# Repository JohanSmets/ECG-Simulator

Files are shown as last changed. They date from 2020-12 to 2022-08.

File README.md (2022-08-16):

# ECG-Simulator
 Electronics, Software and 3D Printable Enclosure of the ECG Patient Simulator based on an Atmega328.
 The simulator has 8 selectable heartrates going from 30 to 240 Bpm.  Works with a 9V battery and has an auto power off function.  This project consists of a Full KiCad project with schematic and PCB,  an Arduino sketch and all the 3D-printable files to make an enclosure.

 This project is licensed under Creative Commons Attribution Share-Alike International Licence 4.0

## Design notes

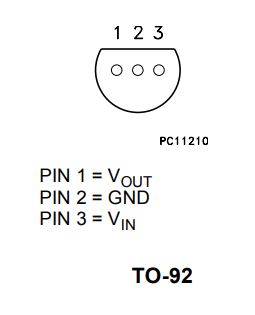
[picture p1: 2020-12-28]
Documentation/Data Sheets and Images/LE50ABZ 5V Regulator Bottom View.JPG

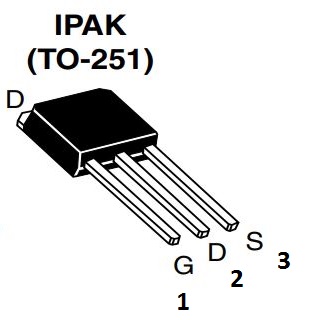
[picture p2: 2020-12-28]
Documentation/Data Sheets and Images/IRFU9024.JPG

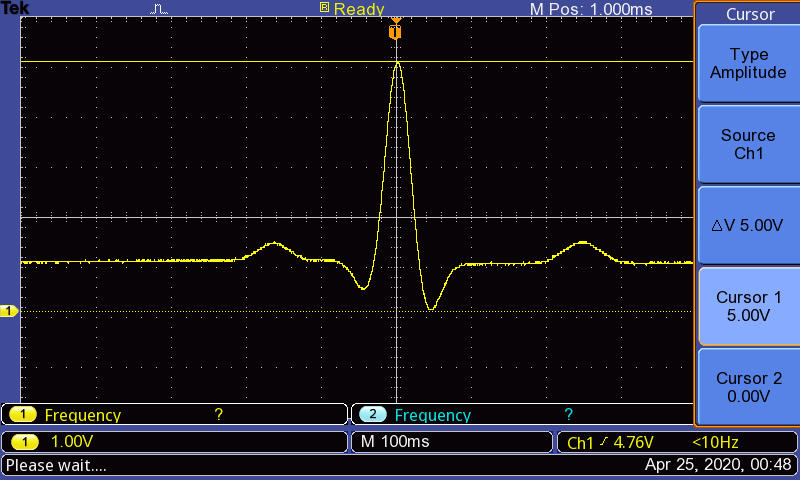
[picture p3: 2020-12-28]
SCOPE_WAVES/ECG Simulator/Signal out of function generator/F0003TEK.BMP

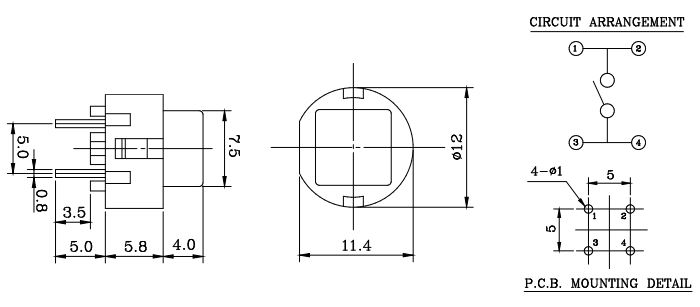
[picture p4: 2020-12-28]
Documentation/Data Sheets and Images/PushButton 532000007 Data.JPG

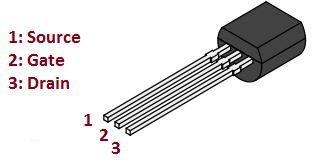
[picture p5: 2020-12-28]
Documentation/Data Sheets and Images/2N7000.JPG

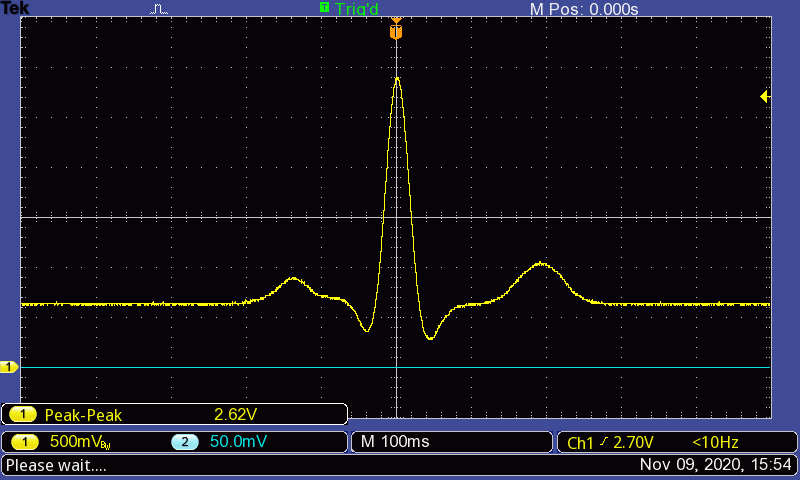
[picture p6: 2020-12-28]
SCOPE_WAVES/ECG Simulator/Signal behind Low Pass Filters with maximal gain selected/F0001TEK.BMP

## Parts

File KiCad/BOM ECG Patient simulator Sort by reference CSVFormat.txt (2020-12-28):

"Source:","C:\Users\Johan\Documents\Arduino\Projecten\ECG Simulator\KiCad ECG Patient simulator\ECG Patient simulator.sch"
"Date:","14/11/2020 13:45:55"
"Tool:","Eeschema (5.1.0)-1"
"Component Count:","41"
"Ref","Value","Footprint","Datasheet","Manufacturer","Vendor"
"C1","10uF","Capacitor_THT:CP_Radial_D6.3mm_P2.50mm","~","",""
"C2","2,2uF","Capacitor_THT:CP_Radial_D6.3mm_P2.50mm","~","",""
"C3","100nF","Capacitor_THT:C_Disc_D5.0mm_W2.5mm_P5.00mm","~","",""
"C4","100nF","Capacitor_THT:C_Disc_D5.0mm_W2.5mm_P5.00mm","~","",""
"C5","22pF","Capacitor_THT:C_Disc_D5.0mm_W2.5mm_P5.00mm","~","",""
"C6","22pF","Capacitor_THT:C_Disc_D5.0mm_W2.5mm_P5.00mm","~","",""
"C7","200nF","Capacitor_THT:C_Disc_D5.0mm_W2.5mm_P5.00mm","~","",""
"C8","47nF","Capacitor_THT:C_Disc_D5.0mm_W2.5mm_P5.00mm","~","",""
"C9","1uF","Capacitor_THT:CP_Radial_D6.3mm_P2.50mm","~","",""
"D1","1N4148","Diode_THT:D_DO-35_SOD27_P7.62mm_Horizontal","https://assets.nexperia.com/documents/data-sheet/1N4148_1N4448.pdf","",""
"D2","1N4148","Diode_THT:D_DO-35_SOD27_P7.62mm_Horizontal","https://assets.nexperia.com/documents/data-sheet/1N4148_1N4448.pdf","",""
"D3","1N4148","Diode_THT:D_DO-35_SOD27_P7.62mm_Horizontal","~","",""
"D4","1N4148","Diode_THT:D_DO-35_SOD27_P7.62mm_Horizontal","https://assets.nexperia.com/documents/data-sheet/1N4148_1N4448.pdf","",""
"D5","1N4001","Diode_THT:D_DO-41_SOD81_P10.16mm_Horizontal","http://www.vishay.com/docs/88503/1n4001.pdf","",""
"D6","LED","LED_THT:LED_D5.0mm","~","",""
"J1","Battery Connector","Connector_PinHeader_2.54mm:PinHeader_1x02_P2.54mm_Vertical","~","",""
"J2","LeadWire Connector","Connector_PinSocket_2.54mm:PinSocket_2x05_P2.54mm_Vertical","~","",""
"J3","Speaker Connector","Connector_PinHeader_2.54mm:PinHeader_1x02_P2.54mm_Vertical","~","",""
"J4","Att Resistor","Connector_PinHeader_2.54mm:PinHeader_1x05_P2.54mm_Vertical","~","",""
"Q1","IRFU9024","Package_TO_SOT_THT:TO-251-3_Vertical","","",""
"Q2","2N7000","Package_TO_SOT_THT:TO-92_Inline","https://www.fairchildsemi.com/datasheets/2N/2N7000.pdf","",""
"Q3","2N7000","Package_TO_SOT_THT:TO-92_Inline","https://www.fairchildsemi.com/datasheets/2N/2N7000.pdf","",""
"R1","56K","Resistor_THT:R_Axial_DIN0207_L6.3mm_D2.5mm_P10.16mm_Horizontal","~","",""
"R2","56K","Resistor_THT:R_Axial_DIN0207_L6.3mm_D2.5mm_P10.16mm_Horizontal","~","",""
"R3","220R","Resistor_THT:R_Axial_DIN0207_L6.3mm_D2.5mm_P10.16mm_Horizontal","~","",""
"R4","10K","Resistor_THT:R_Axial_DIN0207_L6.3mm_D2.5mm_P10.16mm_Horizontal","~","",""
"R5","5K6","Resistor_THT:R_Axial_DIN0207_L6.3mm_D2.5mm_P10.16mm_Horizontal","~","",""
"R6","2K7","Resistor_THT:R_Axial_DIN0207_L6.3mm_D2.5mm_P10.16mm_Horizontal","~","",""
"R7","10K","Resistor_THT:R_Axial_DIN0207_L6.3mm_D2.5mm_P10.16mm_Horizontal","~","",""
"R8","1K","Resistor_THT:R_Axial_DIN0207_L6.3mm_D2.5mm_P10.16mm_Horizontal","~","",""
"R9","330K","Resistor_THT:R_Axial_DIN0207_L6.3mm_D2.5mm_P10.16mm_Horizontal","~","",""
"R10","330R","Resistor_THT:R_Axial_DIN0207_L6.3mm_D2.5mm_P10.16mm_Horizontal","~","",""
"R11","27R","Resistor_THT:R_Axial_DIN0207_L6.3mm_D2.5mm_P10.16mm_Horizontal","~","",""
"R12","82R","Resistor_THT:R_Axial_DIN0207_L6.3mm_D2.5mm_P10.16mm_Horizontal","~","",""
"R13","390R","Resistor_THT:R_Axial_DIN0207_L6.3mm_D2.5mm_P10.16mm_Horizontal","~","",""
"SW1","UP","Button_Switch_THT:Push_E-Switch_KS01Q01","","",""
"SW2","DOWN","Button_Switch_THT:Push_E-Switch_KS01Q01","","",""
"SW4","DIP_x02","Package_DIP:DIP-4_W7.62mm","~","",""
"U1","ATmega328-PU","Package_DIP:DIP-28_W7.62mm","http://ww1.microchip.com/downloads/en/DeviceDoc/ATmega328_P%20AVR%20MCU%20with%20picoPower%20Technology%20Data%20Sheet%2040001984A.pdf","",""
"U2","LE50ABZ","Package_TO_SOT_THT:TO-92_Inline_Wide","","",""
"Y1","16Mhz","Crystal:Crystal_HC18-U_Vertical","~","",""

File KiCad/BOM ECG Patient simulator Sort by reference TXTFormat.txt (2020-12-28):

Source:	C:\Users\Johan\Documents\Arduino\Projecten\ECG Simulator\KiCad ECG Patient simulator\ECG Patient simulator.sch
Date:	14/11/2020 13:43:31
Tool:	Eeschema (5.1.0)-1
Component Count:	41
Ref	Value	Part	Footprint	Description	Vendor
C1	10uF	Device:CP	Capacitor_THT:CP_Radial_D6.3mm_P2.50mm	Polarized capacitor	
C2	2,2uF	Device:CP	Capacitor_THT:CP_Radial_D6.3mm_P2.50mm	Polarized capacitor	
C3	100nF	Device:C	Capacitor_THT:C_Disc_D5.0mm_W2.5mm_P5.00mm	Unpolarized capacitor	
C4	100nF	Device:C	Capacitor_THT:C_Disc_D5.0mm_W2.5mm_P5.00mm	Unpolarized capacitor	
C5	22pF	Device:C	Capacitor_THT:C_Disc_D5.0mm_W2.5mm_P5.00mm	Unpolarized capacitor	
C6	22pF	Device:C	Capacitor_THT:C_Disc_D5.0mm_W2.5mm_P5.00mm	Unpolarized capacitor	
C7	200nF	Device:C	Capacitor_THT:C_Disc_D5.0mm_W2.5mm_P5.00mm	Unpolarized capacitor	
C8	47nF	Device:C	Capacitor_THT:C_Disc_D5.0mm_W2.5mm_P5.00mm	Unpolarized capacitor	
C9	1uF	Device:CP_Small	Capacitor_THT:CP_Radial_D6.3mm_P2.50mm	Polarized capacitor, small symbol	
D1	1N4148	Diode:1N4148	Diode_THT:D_DO-35_SOD27_P7.62mm_Horizontal	100V 0.15A standard switching diode, DO-35	
D2	1N4148	Diode:1N4148	Diode_THT:D_DO-35_SOD27_P7.62mm_Horizontal	100V 0.15A standard switching diode, DO-35	
D3	1N4148	Device:D	Diode_THT:D_DO-35_SOD27_P7.62mm_Horizontal	Diode	
D4	1N4148	Diode:1N4148	Diode_THT:D_DO-35_SOD27_P7.62mm_Horizontal	100V 0.15A standard switching diode, DO-35	
D5	1N4001	Diode:1N4001	Diode_THT:D_DO-41_SOD81_P10.16mm_Horizontal	50V 1A General Purpose Rectifier Diode, DO-41	
D6	LED	Device:LED	LED_THT:LED_D5.0mm	Light emitting diode	
J1	Battery Connector	Connector_Generic:Conn_01x02	Connector_PinHeader_2.54mm:PinHeader_1x02_P2.54mm_Vertical	Generic connector, single row, 01x02, script generated (kicad-library-utils/schlib/autogen/connector/)	
J2	LeadWire Connector	Connector_Generic:Conn_02x05_Odd_Even	Connector_PinSocket_2.54mm:PinSocket_2x05_P2.54mm_Vertical	Generic connector, double row, 02x05, odd/even pin numbering scheme (row 1 odd numbers, row 2 even numbers), script generated (kicad-library-utils/schlib/autogen/connector/)	
J3	Speaker Connector	Connector_Generic:Conn_01x02	Connector_PinHeader_2.54mm:PinHeader_1x02_P2.54mm_Vertical	Generic connector, single row, 01x02, script generated (kicad-library-utils/schlib/autogen/connector/)	
J4	Att Resistor	Connector_Generic:Conn_01x05	Connector_PinHeader_2.54mm:PinHeader_1x05_P2.54mm_Vertical	Generic connector, single row, 01x05, script generated (kicad-library-utils/schlib/autogen/connector/)	
Q1	IRFU9024	Transistor_FET:IRFU9024	Package_TO_SOT_THT:TO-251-3_Vertical	-5A Id, -60V Vds, 0,28Ohm Rds, P-Channel MOSFET	
Q2	2N7000	Transistor_FET:2N7000	Package_TO_SOT_THT:TO-92_Inline	0.2A Id, 200V Vds, N-Channel MOSFET, 2.6V Logic Level, TO-92	
Q3	2N7000	Transistor_FET:2N7000	Package_TO_SOT_THT:TO-92_Inline	0.2A Id, 200V Vds, N-Channel MOSFET, 2.6V Logic Level, TO-92	
R1	56K	Device:R	Resistor_THT:R_Axial_DIN0207_L6.3mm_D2.5mm_P10.16mm_Horizontal	Resistor	
R2	56K	Device:R	Resistor_THT:R_Axial_DIN0207_L6.3mm_D2.5mm_P10.16mm_Horizontal	Resistor	
R3	220R	Device:R	Resistor_THT:R_Axial_DIN0207_L6.3mm_D2.5mm_P10.16mm_Horizontal	Resistor	
R4	10K	Device:R	Resistor_THT:R_Axial_DIN0207_L6.3mm_D2.5mm_P10.16mm_Horizontal	Resistor	
R5	5K6	Device:R	Resistor_THT:R_Axial_DIN0207_L6.3mm_D2.5mm_P10.16mm_Horizontal	Resistor	
R6	2K7	Device:R	Resistor_THT:R_Axial_DIN0207_L6.3mm_D2.5mm_P10.16mm_Horizontal	Resistor	
R7	10K	Device:R	Resistor_THT:R_Axial_DIN0207_L6.3mm_D2.5mm_P10.16mm_Horizontal	Resistor	
R8	1K	Device:R	Resistor_THT:R_Axial_DIN0207_L6.3mm_D2.5mm_P10.16mm_Horizontal	Resistor	
R9	330K	Device:R	Resistor_THT:R_Axial_DIN0207_L6.3mm_D2.5mm_P10.16mm_Horizontal	Resistor	
R10	330R	Device:R	Resistor_THT:R_Axial_DIN0207_L6.3mm_D2.5mm_P10.16mm_Horizontal	Resistor	
R11	27R	Device:R	Resistor_THT:R_Axial_DIN0207_L6.3mm_D2.5mm_P10.16mm_Horizontal	Resistor	
R12	82R	Device:R	Resistor_THT:R_Axial_DIN0207_L6.3mm_D2.5mm_P10.16mm_Horizontal	Resistor	
R13	390R	Device:R	Resistor_THT:R_Axial_DIN0207_L6.3mm_D2.5mm_P10.16mm_Horizontal	Resistor	
SW1	UP	Switch:SW_Push_Dual_x2	Button_Switch_THT:Push_E-Switch_KS01Q01	Push button switch, generic, separate symbols, four pins	
SW2	DOWN	Switch:SW_Push_Dual_x2	Button_Switch_THT:Push_E-Switch_KS01Q01	Push button switch, generic, separate symbols, four pins	
SW4	DIP_x02	Switch:SW_DIP_x02	Package_DIP:DIP-4_W7.62mm	2x DIP Switch, Single Pole Single Throw (SPST) switch, small symbol	
U1	ATmega328-PU	MCU_Microchip_ATmega:ATmega328-PU	Package_DIP:DIP-28_W7.62mm	20MHz, 32kB Flash, 2kB SRAM, 1kB EEPROM, DIP-28	
U2	LE50ABZ	Regulator_Linear:LE50ABZ	Package_TO_SOT_THT:TO-92_Inline_Wide	5V Voltage Regulator Low voltage Drop 100mA	
Y1	16Mhz	Device:Crystal	Crystal:Crystal_HC18-U_Vertical	Two pin crystal

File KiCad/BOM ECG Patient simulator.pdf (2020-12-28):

ECG Patient Simulator | BILL OF MATERIAL
Ref. | Quantity Type | Value | Footprint
C1 | 1 | Capacitor Electrolytic | 10uF | Capacitor_THT:CP_Radial_D6.3mm_P2.50mm
C2 | 1 | Capacitor Electrolytic | 2,2uF | Capacitor_THT:CP_Radial_D6.3mm_P2.50mm
C3, C4 | 2 | Capacitor Ceramic | 100nF | Capacitor_THT:C_Disc_D5.0mm_W2.5mm_P5.00mm
C5, C6 | 2 | Capacitor Ceramic | 22pF | Capacitor_THT:C_Disc_D5.0mm_W2.5mm_P5.00mm
C7 | 1 | Capacitor Ceramic | 200nF | Capacitor_THT:C_Disc_D5.0mm_W2.5mm_P5.00mm
C8 | 1 | Capacitor Electrolytic | 47nF | Capacitor_THT:C_Disc_D5.0mm_W2.5mm_P5.00mm
C9 | 1 | Capacitor Electrolytic | 1uF | Capacitor_THT:CP_Radial_D6.3mm_P2.50mm
D1, D2, D3, D4 | 4 | Diode DUS | 1N4148 | Diode_THT:D_DO-35_SOD27_P7.62mm_Horizontal
D5 | 1 | Diode Rectifier | 1N4001 or 1N4007 | Diode_THT:D_DO-41_SOD81_P10.16mm_Horizontal
D6 | 1 | LED White 5mm 3,2V 20mALED | LED_THT:LED_D5.0mm
J1 | 1 | PinConnector | Battery Connector | Connector_PinHeader_2.54mm:PinHeader_1x02_P2.54mm_Vertical
J2 | 1 | PinConnector | LeadWire Connector Connector_PinHeader_2.54mm:PinHeader_2x05_P2.54mm_Vertical
J3 | 1 | PinConnector | Speaker Connector | Connector_PinHeader_2.54mm:PinHeader_1x02_P2.54mm_Vertical
J4 | 1 | Att Resistor Socket | Att Resistor Socket | Connector_PinHeader_2.54mm:PinHeader_1x05_P2.54mm_Vertical
Q1 | 1 | MOSFET P-Channel | IRFU9024 | Package_TO_SOT_THT:TO-251-3_Vertical
Q2, Q3 | 2 | MOSFET N-Channel | 2N7000 | Package_TO_SOT_THT:TO-92_Inline
R1, R2 | 2 | Resistor 1/4W 5% | 56K | Resistor_THT:R_Axial_DIN0207_L6.3mm_D2.5mm_P10.16mm_Horizontal
R2 | 1 | Resistor 1/4W 5% | 56K | Resistor_THT:R_Axial_DIN0207_L6.3mm_D2.5mm_P10.16mm_Horizontal
R3 | 1 | Resistor 1/4W 5% | 220R | Resistor_THT:R_Axial_DIN0207_L6.3mm_D2.5mm_P10.16mm_Horizontal
R4, R7 | 2 | Resistor 1/4W 5% | 10K | Resistor_THT:R_Axial_DIN0207_L6.3mm_D2.5mm_P10.16mm_Horizontal
R5 | 1 | Resistor 1/4W 5% | 5K6 | Resistor_THT:R_Axial_DIN0207_L6.3mm_D2.5mm_P10.16mm_Horizontal
R6 | 1 | Resistor 1/4W 5% | 2K7 | Resistor_THT:R_Axial_DIN0207_L6.3mm_D2.5mm_P10.16mm_Horizontal
R8 | 1 | Resistor 1/4W 5% | 1K | Resistor_THT:R_Axial_DIN0207_L6.3mm_D2.5mm_P10.16mm_Horizontal
R9 | 1 | Resistor 1/4W 5% | 330K | Resistor_THT:R_Axial_DIN0207_L6.3mm_D2.5mm_P10.16mm_Horizontal
R10 | 1 | Resistor 1/4W 5% | 330R | Resistor_THT:R_Axial_DIN0207_L6.3mm_D2.5mm_P10.16mm_Horizontal

Date: 14/11/2020 13:43:31
Tool: Eeschema (5.1.0)-1
Component Count: 50

R11 | 1 | Resistor 1/4W 5% | 27R | Resistor_THT:R_Axial_DIN0207_L6.3mm_D2.5mm_P10.16mm_Horizontal
R12 | 1 | Resistor 1/4W 5% | 82R | Resistor_THT:R_Axial_DIN0207_L6.3mm_D2.5mm_P10.16mm_Horizontal
R13 | 1 | Resistor 1/4W 5% | 390R | Resistor_THT:R_Axial_DIN0207_L6.3mm_D2.5mm_P10.16mm_Horizontal
SW1, SW2 | 2 | PushButton BROSE 532.000.007 UP, DOWN Switch | Button_Switch_THT:Push_E-Switch_KS01Q01
SW4 | 1 | Dip Switch 2 position | DIP_x02 | Package_DIP:DIP-4_W7.62mm
U1 | 1 | Microcontroller Arduino Bootloaded ATmega328-PU | Package_DIP:DIP-28_W7.62mm
U2 | 1 | Linear Voltage regulator LE50ABZ | Package_TO_SOT_THT:TO-92_Inline_Wide
Y1 | 1 | Low Profile X-Tal | 16Mhz | Crystal:Crystal_HC18-U_Vertical

PCB and External Components
Speaker Att. Res | 1 | Resistor 1/4W 5% | Typically 100R | Resitor_THT:R_Axial_DIN0207_L6.3mm_D2.5mm_P10.16mm_Horizontal
9V Battery Clip | 1 | 9V Battery Clip
10-Pole IDC Connector1 | 10-Pole IDC Connector
20 mm Speaker | 1 | 20 mm Speaker | Piezo Speaker 20mm
28 Pin IC Socket | 1 | 28 Pin IC Socket | | Package_DIP:DIP-28_W7.62mm
Female Header | 2 | Female Header | | Female header for pushbutton extension
PCB Eurocircuits | 1 | PCB Eurocircuits

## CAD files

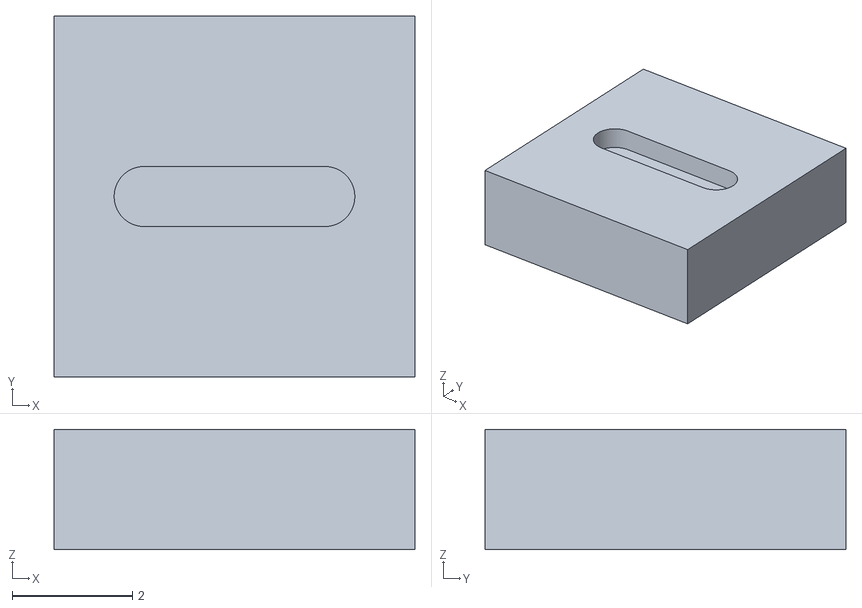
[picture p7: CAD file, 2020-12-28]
RS DesignSpark Mechanical/ECG Minus Inlay - Invallende Tekst.stl
6.00 x 6.00 x 2.00

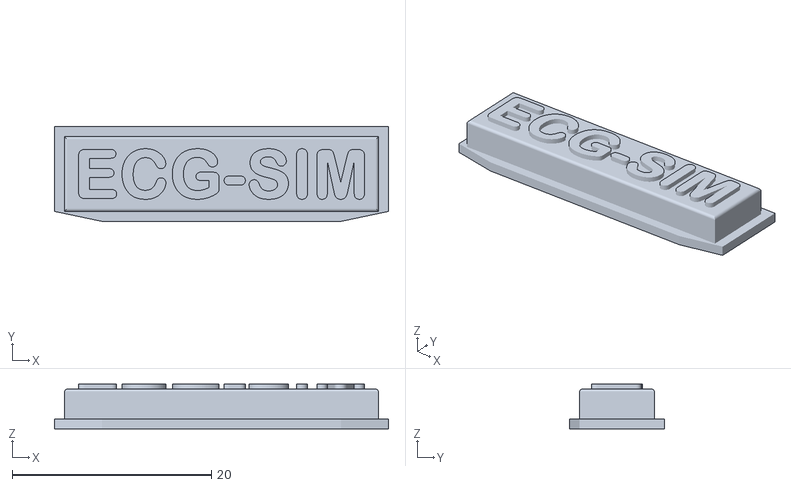
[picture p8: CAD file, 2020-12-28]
RS DesignSpark Mechanical/ECG ECG-SIM Inlay - Opliggende Tekst.stl
33.5 x 9.50 x 4.50

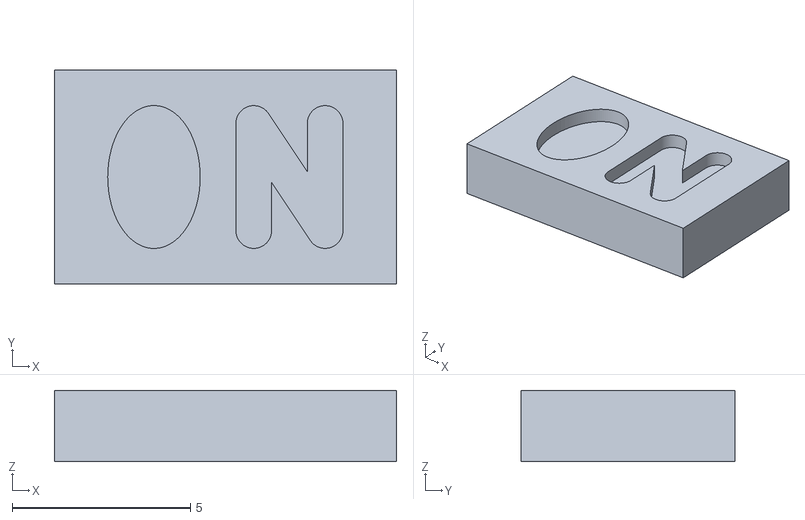
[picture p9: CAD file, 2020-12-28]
RS DesignSpark Mechanical/ECG ON inlay - Invallende Tekst.stl
9.58 x 6.00 x 2.00

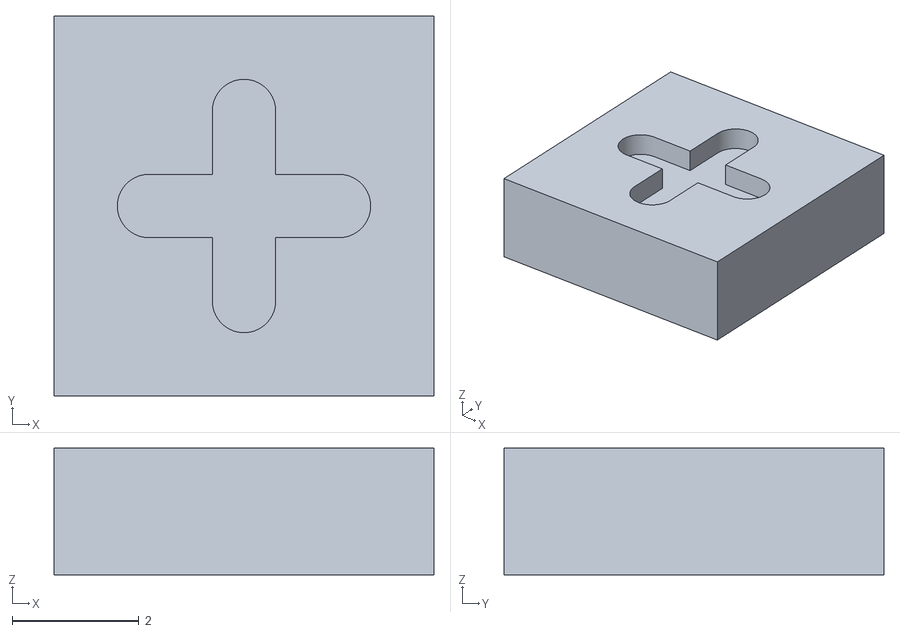
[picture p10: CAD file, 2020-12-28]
RS DesignSpark Mechanical/ECG Plus Inlay - Invallende Tekst.stl
6.00 x 6.00 x 2.00

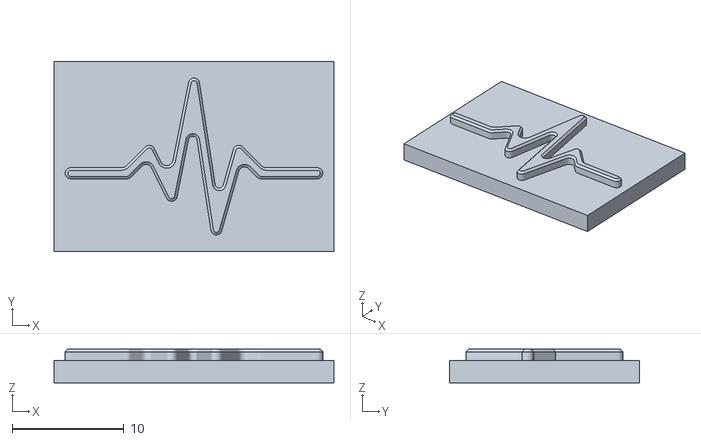
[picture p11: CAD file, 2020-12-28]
RS DesignSpark Mechanical/ECG WaveForm Inlay.stl
25.0 x 17.0 x 3.00

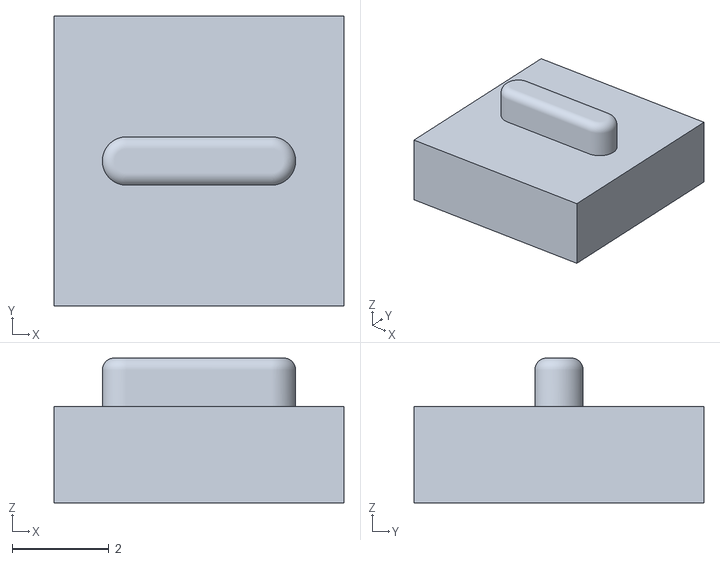
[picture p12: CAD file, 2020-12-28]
RS DesignSpark Mechanical/ECG Minus Inlay - Opliggende Tekst.stl
6.00 x 6.00 x 3.00

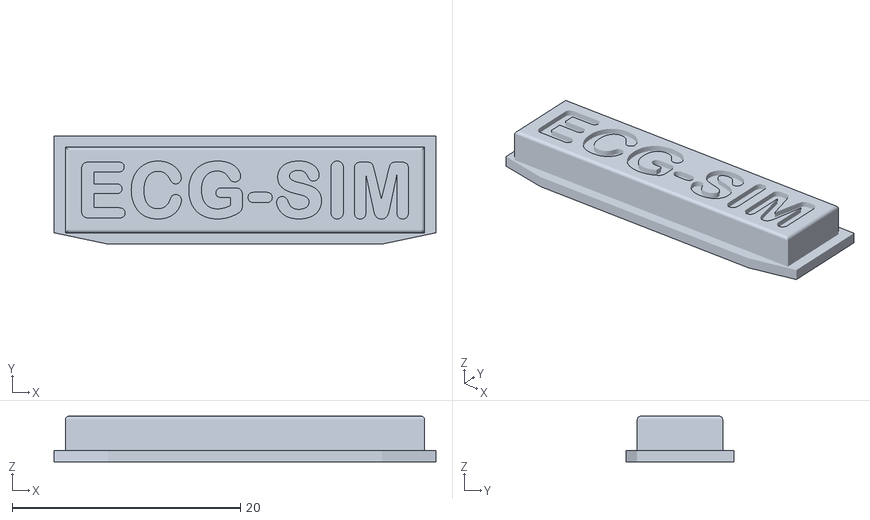
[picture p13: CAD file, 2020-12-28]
RS DesignSpark Mechanical/ECG ECG-SIM Inlay - Invallende Tekst.stl
33.5 x 9.50 x 4.00

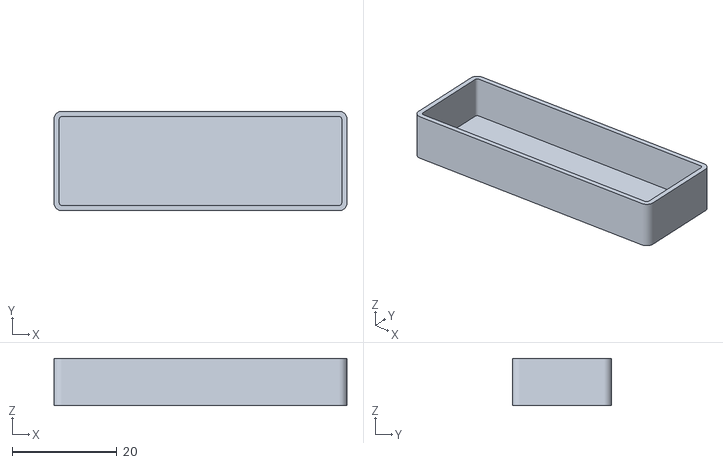
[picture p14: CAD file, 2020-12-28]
RS DesignSpark Mechanical/ECG Battery Cover.stl
56.0 x 19.0 x 9.00

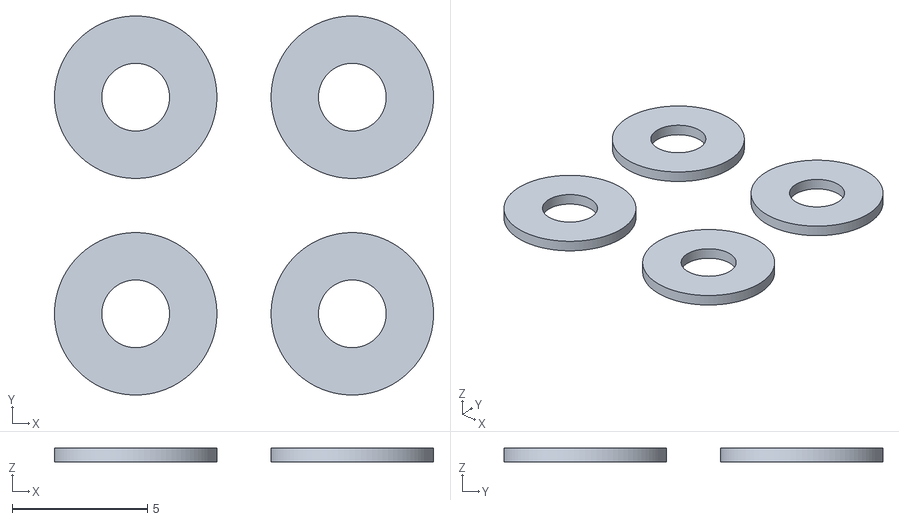
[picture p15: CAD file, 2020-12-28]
RS DesignSpark Mechanical/Afstandsbusjes 2_5 mm - 6_0 mm - H 0_5 mm (4 Stuks).stl
14.0 x 14.0 x 0.5

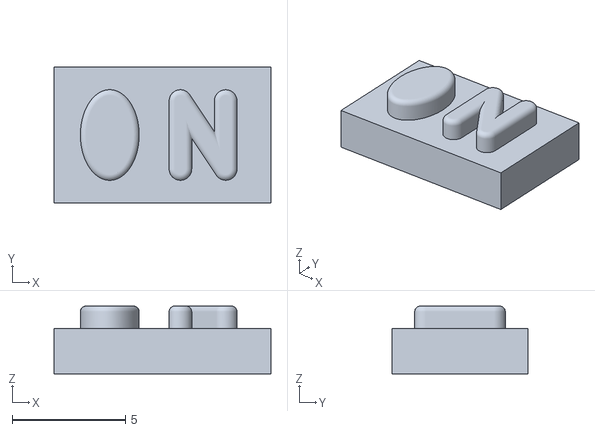
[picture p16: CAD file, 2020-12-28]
RS DesignSpark Mechanical/ECG ON inlay - Opliggende Tekst.stl
9.58 x 6.00 x 3.00

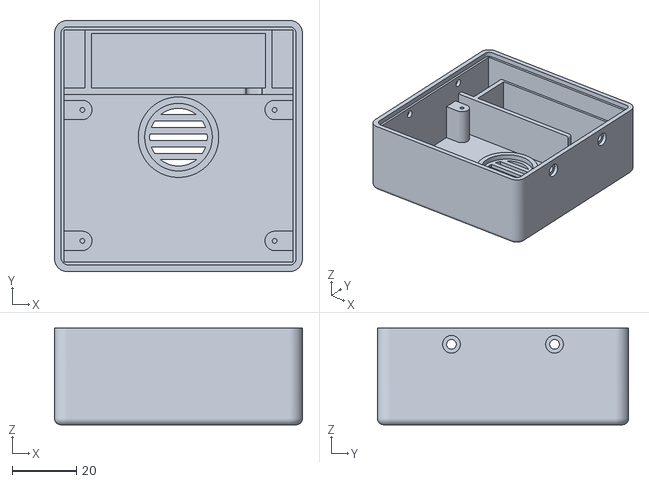
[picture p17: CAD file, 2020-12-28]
RS DesignSpark Mechanical/ECG Bottom Case.stl
77.0 x 78.0 x 30.0

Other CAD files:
RS DesignSpark Mechanical/ECG Plus Inlay - Opliggende Tekst.stl

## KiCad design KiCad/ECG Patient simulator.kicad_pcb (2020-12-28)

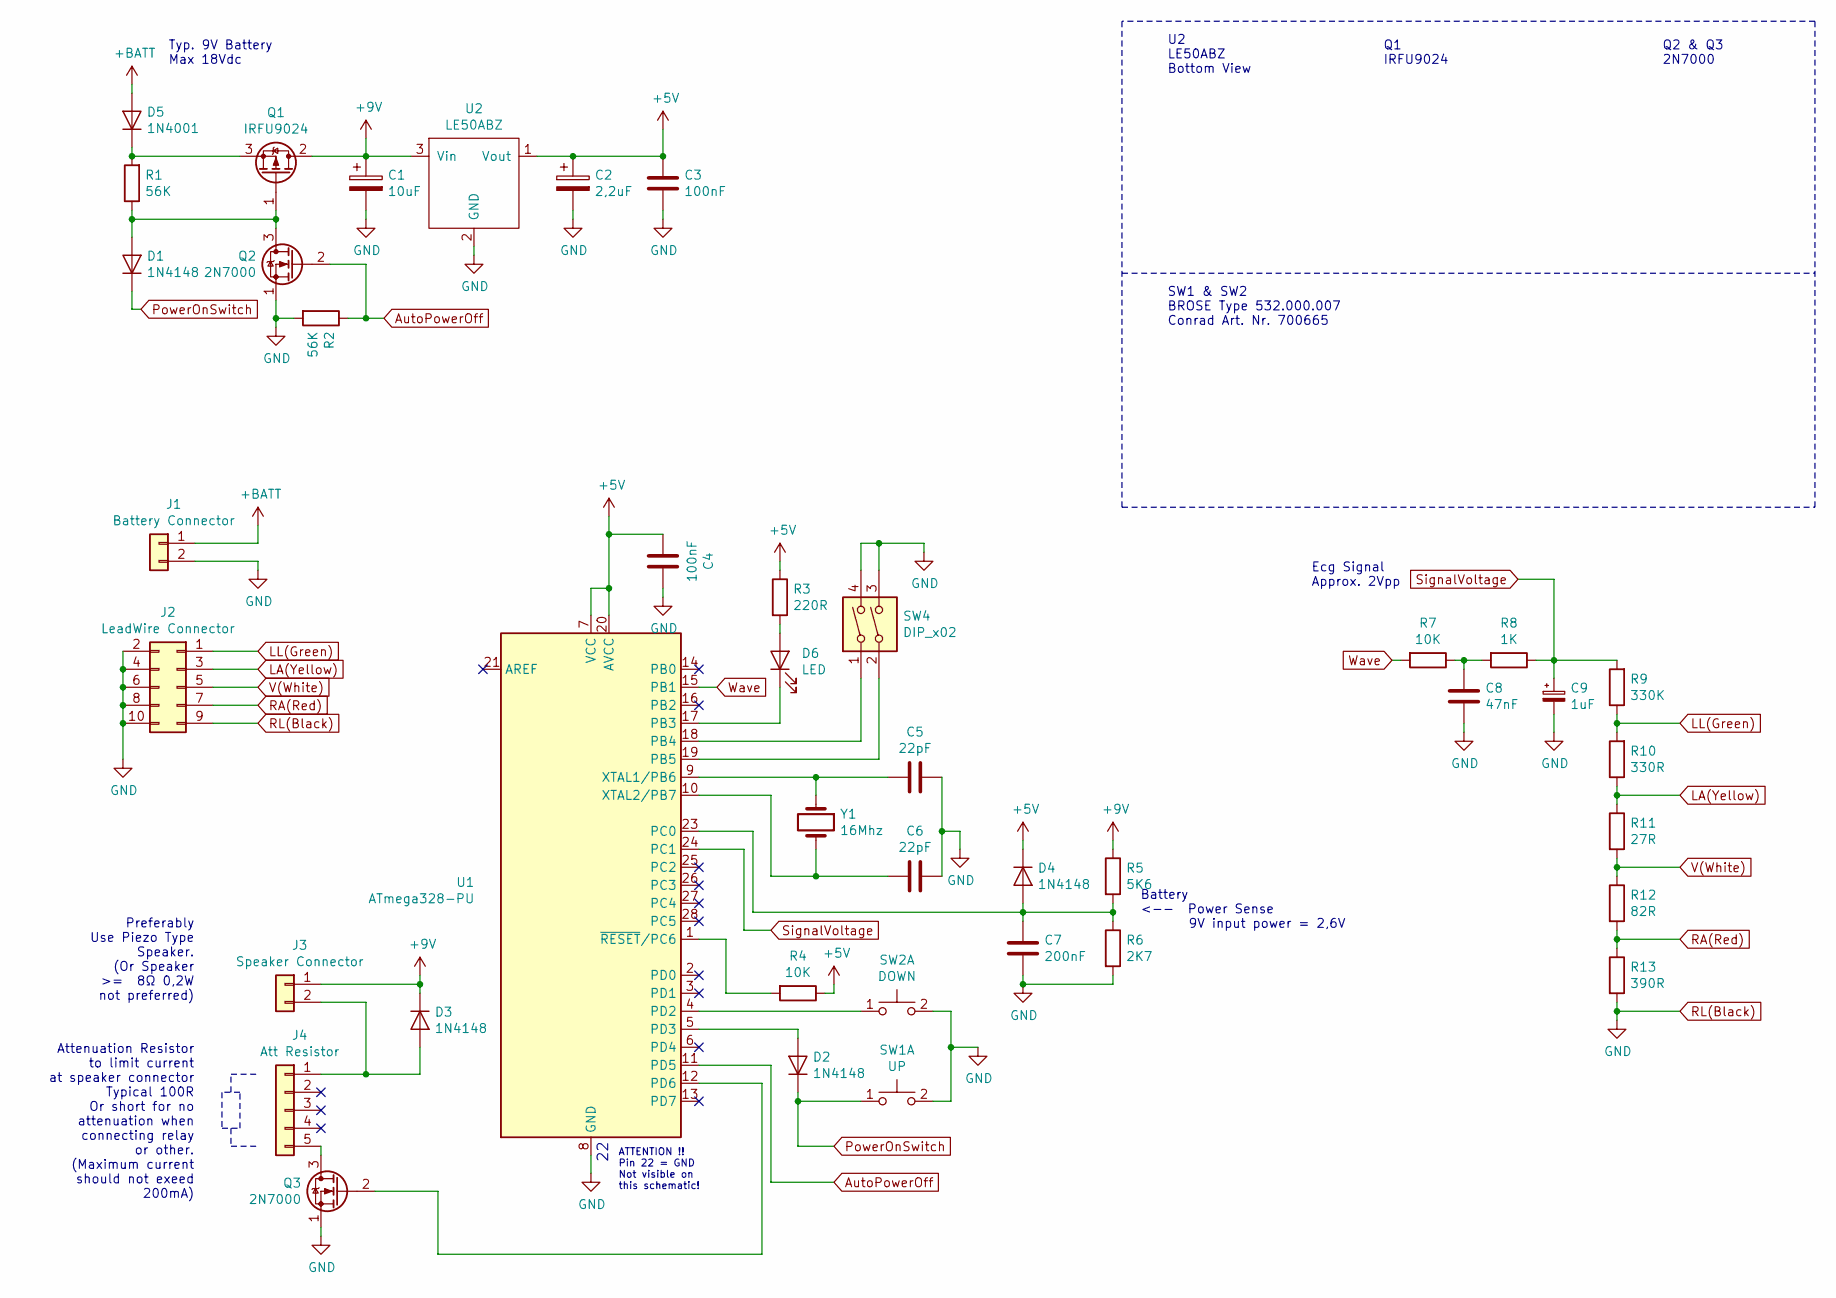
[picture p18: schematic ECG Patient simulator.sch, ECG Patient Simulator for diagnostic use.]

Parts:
C1: 10uF; CP_Radial_D6.3mm_P2.50mm
C2: 2,2uF; CP_Radial_D6.3mm_P2.50mm
C3, C4: 100nF; C_Disc_D5.0mm_W2.5mm_P5.00mm
C5, C6: 22pF; C_Disc_D5.0mm_W2.5mm_P5.00mm
C7: 200nF; C_Disc_D5.0mm_W2.5mm_P5.00mm
C8: 47nF; C_Disc_D5.0mm_W2.5mm_P5.00mm
C9: 1uF; CP_Radial_D6.3mm_P2.50mm
D1, D2, D3, D4: 1N4148; D_DO-35_SOD27_P7.62mm_Horizontal
D5: 1N4001; D_DO-41_SOD81_P10.16mm_Horizontal
D6: LED; LED_D5.0mm
J1: Battery Connector; PinHeader_1x02_P2.54mm_Vertical
J2: LeadWire Connector; PinSocket_2x05_P2.54mm_Vertical
J3: Speaker Connector; PinHeader_1x02_P2.54mm_Vertical
J4: Att Resistor; PinHeader_1x05_P2.54mm_Vertical
Q1: IRFU9024; TO-251-3_Vertical
Q2, Q3: 2N7000; TO-92_Inline
R1, R2: 56K; R_Axial_DIN0207_L6.3mm_D2.5mm_P10.16mm_Horizontal
R3: 220R; R_Axial_DIN0207_L6.3mm_D2.5mm_P10.16mm_Horizontal
R4, R7: 10K; R_Axial_DIN0207_L6.3mm_D2.5mm_P10.16mm_Horizontal
R5: 5K6; R_Axial_DIN0207_L6.3mm_D2.5mm_P10.16mm_Horizontal
R6: 2K7; R_Axial_DIN0207_L6.3mm_D2.5mm_P10.16mm_Horizontal
R8: 1K; R_Axial_DIN0207_L6.3mm_D2.5mm_P10.16mm_Horizontal
R9: 330K; R_Axial_DIN0207_L6.3mm_D2.5mm_P10.16mm_Horizontal
R10: 330R; R_Axial_DIN0207_L6.3mm_D2.5mm_P10.16mm_Horizontal
R11: 27R; R_Axial_DIN0207_L6.3mm_D2.5mm_P10.16mm_Horizontal
R12: 82R; R_Axial_DIN0207_L6.3mm_D2.5mm_P10.16mm_Horizontal
R13: 390R; R_Axial_DIN0207_L6.3mm_D2.5mm_P10.16mm_Horizontal
SW1: UP; Push_E-Switch_KS01Q01
SW2: DOWN; Push_E-Switch_KS01Q01
SW4: DIP_x02; DIP-4_W7.62mm
U1: ATmega328-PU; DIP-28_W7.62mm
U2: LE50ABZ; TO-92_Inline_Wide
Y1: 16Mhz; Crystal_HC18-U_Vertical

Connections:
+5V: C2.1, C3.1, C4.2, D4.1 (K), R3.1, R4.1, U1.7 (VCC), U1.20 (AVCC), U2.1 (Vout)
+9V: C1.1, D3.1 (K), J3.1, Q1.2 (D), R5.1, U2.3 (Vin); also elsewhere on the board
+BATT: D5.2 (A), J1.1; also elsewhere on the board
AutoPowerOff: Q2.2 (G), R2.1, U1.11 (PD5)
LA(Yellow): J2.3, R10.1, R11.1
LL(Green): J2.1, R9.1, R10.2
unnamed: C5.2, U1.9 (XTAL1/PB6), Y1.1
unnamed: C6.2, U1.10 (XTAL2/PB7), Y1.2
unnamed: C7.1, D4.2 (A), R5.2, R6.1, U1.23 (PC0)
unnamed: C8.1, R7.1, R8.2
unnamed: D1.2 (A), Q1.1 (G), Q2.3 (D), R1.1
unnamed: D2.2 (A), U1.5 (PD3)
unnamed 12: D3.2 (A), J3.2, J4.1; also elsewhere on the board
unnamed: D5.1 (K), Q1.3 (S), R1.2
unnamed: D6.1 (K), U1.17 (PB3)
unnamed: D6.2 (A), R3.2
unnamed: J4.5, Q3.3 (D)
unnamed: Q3.2 (G), U1.12 (PD6)
unnamed: R4.2, U1.1 (~RESET~/PC6)
unnamed: SW2.1 (C), U1.4 (PD2)
unnamed: SW4.1, U1.18 (PB4)
unnamed: SW4.2, U1.19 (PB5)
PowerOnSwitch: D1.1 (K), D2.1 (K), SW1.1 (C)
RA(Red): J2.7, R12.2, R13.1
RL(Black): C1.2, C2.2, C3.2, C4.1, C5.1, C6.1, C7.2, C8.2, C9.2, J1.2, J2.2, J2.4, J2.6, J2.8, J2.9, J2.10, Q2.1 (S), Q3.1 (S), R2.2, R6.2, R13.2, SW1.2 (D), SW2.2 (D), SW4.3, SW4.4, U1.8 (GND), U1.22 (GND), U2.2 (GND); also elsewhere on the board
SignalVoltage: C9.1, R8.1, R9.2, U1.24 (PC1)
V(White): J2.5, R11.2, R12.1
Wave: R7.2, U1.15 (PB1)

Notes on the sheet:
Battery <-- Power Sense 9V input power = 2,6V
Typ. 9V Battery Max 18Vdc
U2 LE50ABZ Bottom View
Q1 IRFU9024
Q2 & Q3 2N7000
SW1 & SW2 BROSE Type 532.000.007 Conrad Art. Nr. 700665
ATTENTION !! Pin 22 = GND Not visible on this schematic!
Ecg Signal Approx. 2Vpp
Preferably Use Piezo Type Speaker. (Or Speaker >= 8Ω 0,2W not preferred)
Attenuation Resistor to limit current at speaker connector Typical 100R Or short for no attenuation when connecting relay or other. (Maximum current should not exeed 200mA)

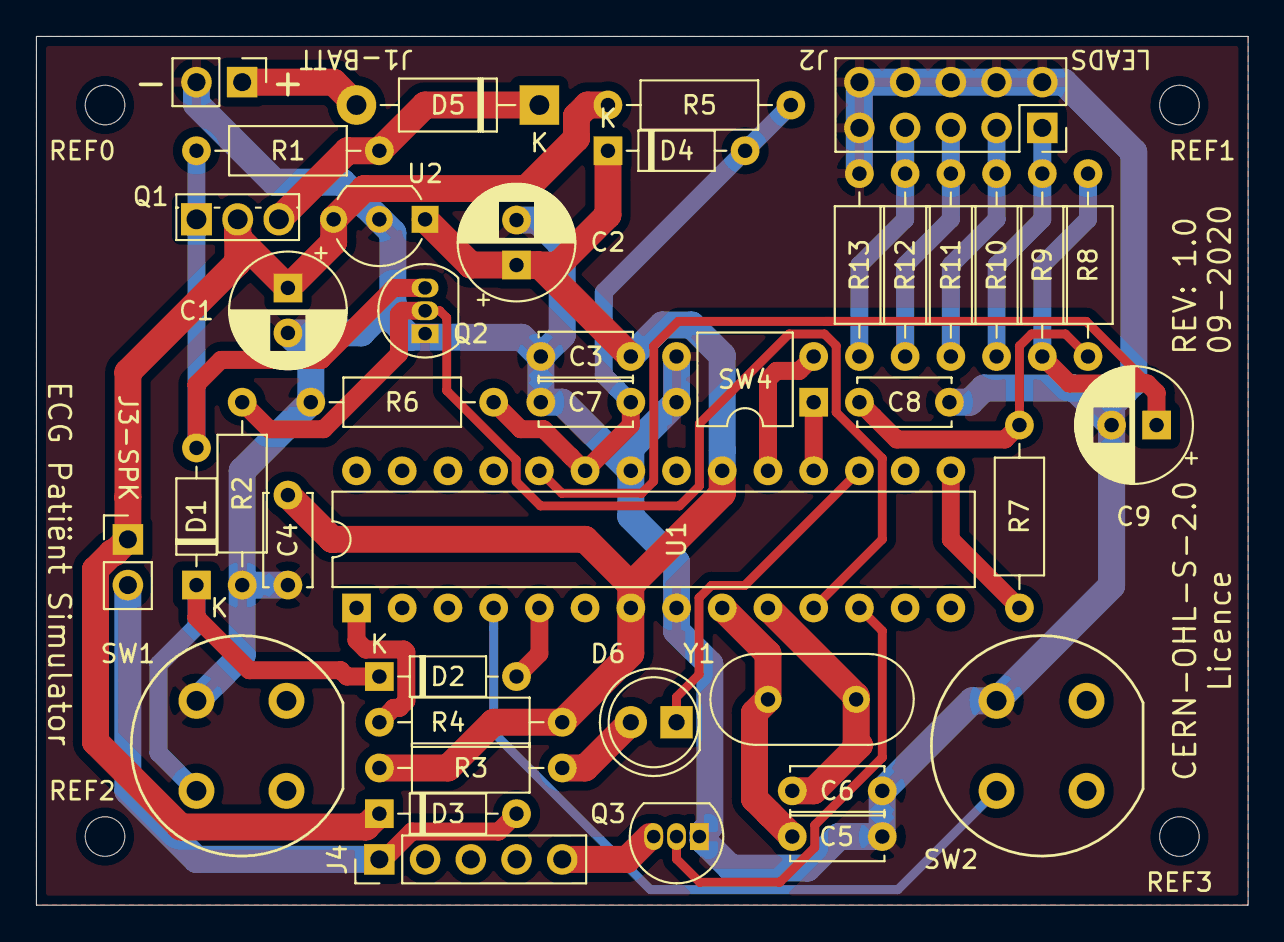
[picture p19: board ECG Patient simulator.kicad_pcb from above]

Board: 2 copper layers, 67.3 x 48.3 mm, 45 parts (0 on the bottom side), 28 nets.

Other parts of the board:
J1-BATT: Battery Connector; PinHeader_1x02_P2.54mm_Vertical
J3-SPK: Speaker Connector; PinHeader_1x02_P2.54mm_Vertical
REF0, REF1, REF2, REF3: MountingHole_2.2mm_M2_ISO7380

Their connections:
+9V: J3-SPK.1; also elsewhere on the board
+BATT: J1-BATT.1; also elsewhere on the board
unnamed 12: J3-SPK.2; also elsewhere on the board
RL(Black): J1-BATT.2; also elsewhere on the board

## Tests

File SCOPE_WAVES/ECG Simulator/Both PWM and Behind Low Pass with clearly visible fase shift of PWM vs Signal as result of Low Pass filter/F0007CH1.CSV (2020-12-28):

Record Length | 2.500000e+03 | -0.122000000000 | 0.00000
Sample Interval | 1.000000e-04 | -0.121900000000 | 0.00000
Trigger Point | 1.220000000000e+03 | -0.121800000000 | 0.00000
 |  | -0.121700000000 | 0.00000
 |  | -0.121600000000 | 50.00000
 |  | -0.121500000000 | 50.00000
Source | CH1 | -0.121400000000 | 0.00000
Vertical Units | V | -0.121300000000 | 0.00000
Vertical Scale | 5.000000e+01 | -0.121200000000 | 0.00000
Vertical Offset | 8.800000e+01 | -0.121100000000 | 0.00000
Horizontal Units | s | -0.121000000000 | 0.00000
Horizontal Scale | 2.500000e-02 | -0.120900000000 | 0.00000
Pt Fmt | Y | -0.120800000000 | 50.00000
Yzero | 0.000000e+00 | -0.120700000000 | 0.00000
Probe Atten | 1.000000e+01 | -0.120600000000 | 2.00000
Model Number | TBS1102B | -0.120500000000 | 2.00000
Serial Number | C021706 | -0.120400000000 | 0.00000
Firmware Version | FV:v4.06 | -0.120300000000 | 0.00000
 |  | -00.120200000000 | 0.00000
 |  | -00.120100000000 | 50.00000
 |  | -00.120000000000 | 0.00000
 |  | -00.119900000000 | 0.00000
 |  | -00.119800000000 | 0.00000
 |  | -00.119700000000 | 0.00000
 |  | -00.119600000000 | 0.00000
 |  | -00.119500000000 | 0.00000
 |  | -00.119400000000 | 50.00000
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

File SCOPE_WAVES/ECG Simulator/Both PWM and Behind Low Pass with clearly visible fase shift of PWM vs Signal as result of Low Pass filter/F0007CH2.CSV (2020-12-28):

Record Length | 2.500000e+03 | -0.122000000000 | 9.40000
Sample Interval | 1.000000e-04 | -0.121900000000 | 9.40000
Trigger Point | 1.220000000000e+03 | -0.121800000000 | 9.40000
 |  | -0.121700000000 | 9.40000
 |  | -0.121600000000 | 9.40000
 |  | -0.121500000000 | 9.40000
Source | CH2 | -0.121400000000 | 9.40000
Vertical Units | V | -0.121300000000 | 9.40000
Vertical Scale | 5.000000e+00 | -0.121200000000 | 9.40000
Vertical Offset | -2.500000e+01 | -0.121100000000 | 9.40000
Horizontal Units | s | -0.121000000000 | 9.40000
Horizontal Scale | 2.500000e-02 | -0.120900000000 | 9.40000
Pt Fmt | Y | -0.120800000000 | 9.40000
Yzero | 0.000000e+00 | -0.120700000000 | 9.20000
Probe Atten | 1.000000e+01 | -0.120600000000 | 9.20000
Model Number | TBS1102B | -0.120500000000 | 9.20000
Serial Number | C021706 | -0.120400000000 | 9.40000
Firmware Version | FV:v4.06 | -0.120300000000 | 9.20000
 |  | -00.120200000000 | 9.40000
 |  | -00.120100000000 | 9.40000
 |  | -00.120000000000 | 9.40000
 |  | -00.119900000000 | 9.40000
 |  | -00.119800000000 | 9.40000
 |  | -00.119700000000 | 9.40000
 |  | -00.119600000000 | 9.40000
 |  | -00.119500000000 | 9.40000
 |  | -00.119400000000 | 9.40000
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

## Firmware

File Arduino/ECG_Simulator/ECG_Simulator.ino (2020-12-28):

/*/////////////////////////////////////////////////////////////////////////////////////////////////////////////////////////////////////////////

---------------------------------------------------------------------------------
|                                                                                 |
| Copyright Johan Smets 2020.                                                     |
|                                                                                 |
| This source is part of the ECG Patient Simulator project and is licensed under  | 
| a Creative Commons Attribution-ShareAlike 4.0 International License.            |
|                                                                                 |
 ---------------------------------------------------------------------------------
 
 ---------------------------------------------------------------------------------
| Copyright Johan Smets 2020.                                                     |
|                                                                                 |
| This program is free software: you can redistribute it and/or modify            |
| it under the terms of the GNU General Public License as published by            |
| the Free Software Foundation, either version 3 of the License, or               |
| any later version.                                                              |
|                                                                                 |
| This program is distributed in the hope that it will be useful,                 |
| but WITHOUT ANY WARRANTY; without even the implied warranty of                  |
| MERCHANTABILITY or FITNESS FOR A PARTICULAR PURPOSE.  See the                   |
| GNU General Public License for more details.                                    |
|                                                                                 |
| You should have received a copy of the GNU General Public License               |
| along with this program.  If not, see <https://www.gnu.org/licenses/>.          |
|                                                                                 |
 --------------------------------------------------------------------------------

 --------------------------------------------------------------------------------------------------------------------------------------
| Copyright Johan Smets 2020.                                                                                                          |
|                                                                                                                                      |
| The, in this source described hardware, if applicable, is Open Hardware and is licensed under the CERN-OHL-S v2 or any later version.|
|                                                                                                                                      |
| You may redistribute and modify the hardware in this source and make products using it under                                         |
| the terms of the CERN-OHL-S v2 or any later version (https://ohwr.org/cern_ohl_s_v2.txt).                                            |
|                                                                                                                                      |
| This source is distributed WITHOUT ANY EXPRESS OR IMPLIED WARRANTY,                                                                  |
| INCLUDING OF MERCHANTABILITY, SATISFACTORY QUALITY AND FITNESS FOR A                                                                 |
| PARTICULAR PURPOSE. Please see the CERN-OHL-S v2 or any later version for applicable conditions.                                     |
|                                                                                                                                      |
| Source location: https://www.steamreactor.be/projecten/ecg-patient-simulator-en/ecg-patient-simulator-one-file-download-en .         |                                  |
|                                                                                                                                      |
| As per CERN-OHL-S v2 section 4, should You produce hardware based on this                                                            |
| source, You must where practicable maintain the Source Location visible                                                              |
| on the external case of the Gizmo or other products you make using this                                                              |
| source.                                                                                                                              |
 --------------------------------------------------------------------------------------------------------------------------------------

 --------------------------------------------------------------------------------------------------------------------------------------
|
| Arduino credentials
|
| This software is developed Using Arduino UNO Hardware and Software.  
| This software is available at the official Arduino website https://www.arduino.cc/ and can be downmloaded and used under the  
| conditions of Arduino company.
|
 --------------------------------------------------------------------------------------------------------------------------------------


Project: ECG Patient Simulator.

Code Version: 1.0
Code Revision: 0
Date (yyyy-mm-dd): 2020-11-12
Related Hardware in development state: Arduino UNO R3
Related Hardware in final version: Self developed PCB (EuroCirquits ref: E1242373) for Atmega328 with Arduino UNO Bootloader.
Related electronics schematic: ECG Patient Simulator for diagnostic use. Rev: 1.0 Date 2020-09-03

Attribution: Designed by: Johan Smets, johan.smets2@gmail.com
Complete project and all related files can be found and downloaded at https://www.steamreactor.be/projecten/ecg-patient-simulator-en

By downloading this(these) file(s) and / or making this project or a derivative of this project, you agree and accept that the designer of this project 
is not responsible for any damage, problems or consequences of any kind that may directly or indirectly be associated with this hardware, 
software and/or intellectual and written content.

FULLY COMMENTED CODE VERSION.
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

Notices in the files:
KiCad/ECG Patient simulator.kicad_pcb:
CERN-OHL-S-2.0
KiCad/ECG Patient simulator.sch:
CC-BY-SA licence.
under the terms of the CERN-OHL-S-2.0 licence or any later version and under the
